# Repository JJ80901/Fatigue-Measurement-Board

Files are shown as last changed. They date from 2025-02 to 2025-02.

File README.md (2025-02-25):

# Fatigue-Measurement-Board
**Precision Displacement Sensing**

This board is designed to process and digitize a ±10V analog signal from a laser displacement sensor, ensuring high-fidelity data acquisition for fatigue testing applications. 

The signal enters through a BNC connector, passes through ESD protection and an RF filter, and is then scaled down to a ±1.65V range using a resistor divider. A non-inverting summing amplifier shifts the signal into a 0-3.3V range, with a 1.65V bias generated by an op-amp follower from a half-resistor divider off the 3.3V power rail.

To prevent aliasing, the conditioned signal passes through a third-order Butterworth Sallen-Key low-pass filter with a 5kHz cutoff frequency, optimized for sampling rates up to 1kHz. The filtered signal is digitized by an ADC141S626 14-bit ADC, which interfaces over SPI with an STM32F103CBT6 microcontroller, responsible for managing data acquisition and transmission.

Power is regulated using a TLV62569 switching regulator for 3.3V conversion and an HT7533-1 LDO, ensuring clean and stable power for the analog front end and microcontroller. 

This design improves upon earlier iterations by incorporating better filtering, precise voltage scaling, and a high-resolution ADC, making it ideal for fatigue analysis, precision displacement measurement, and other high-accuracy signal acquisition applications.

---

### What you'll find in this repository:
- Hardware designs (made in KiCad)
- STM32 Application Notes
- Device datasheets
- Circuit simulations

---

### Repository Project Structure:
- *3D Models* - Models for PCB components not found in the standard KiCad library
- *BOM* - An interactive HTML bill of materials (generated from the *Interactive HTML BOM* Plugin)
- *Datasheets* - Datasheets for specific devices used, such as the buck converter, LDO, Op-Amp, etc.
- *Docs* - STM32 application notes for crystal and USB design
- *Fatigue Test Board* - KiCad design files
- *Images* - High quality renderings of the final PCB in 3D
- *Libraries* - Folders to include schematic symbols and footprints for components not found in the standard KiCad library
- *Outputs* - Gerber files for manufacturing the PCB
- *Schematics* - PDFs of entire PCB schematic
- *Simulations* - LTSpice simulation block with any custom component libraries

---
***Disclaimer**: This board is ordered, but not yet tested!*

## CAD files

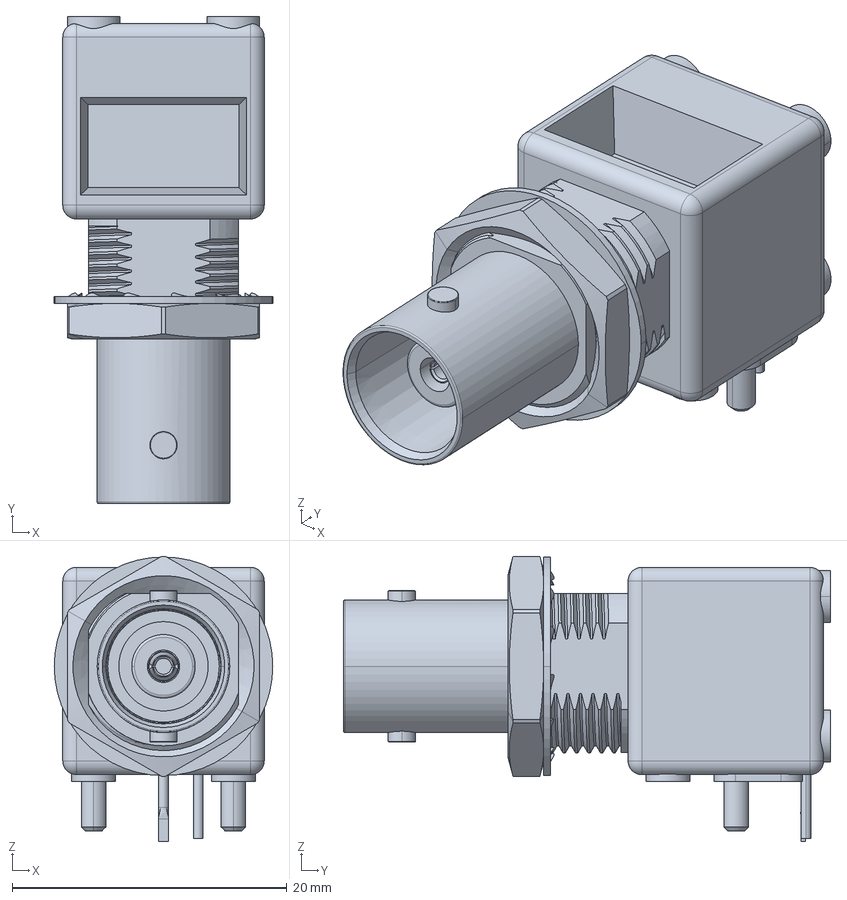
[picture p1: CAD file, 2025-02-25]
3D Models/BNC.stp
15.9 x 35.4 x 20.8 mm

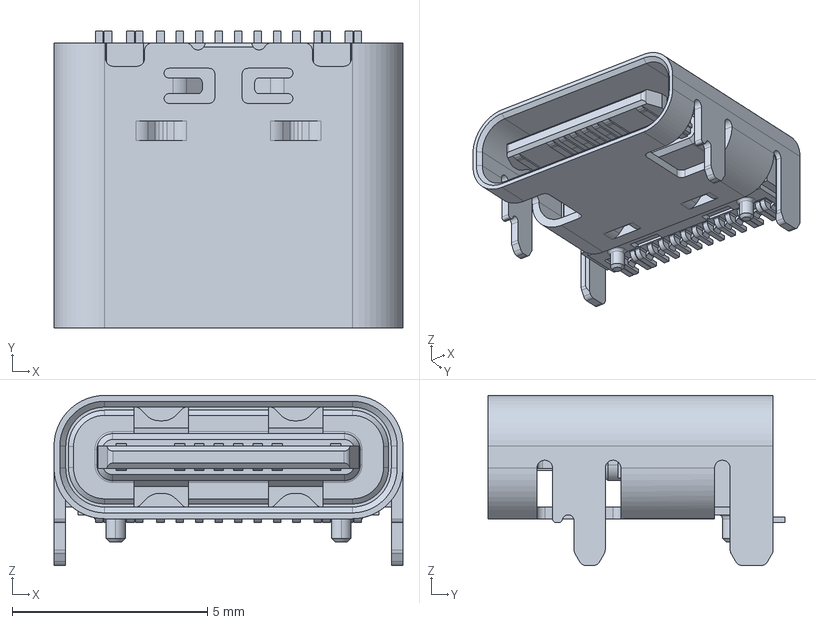
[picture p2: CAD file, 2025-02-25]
3D Models/USB-C.stp
8.94 x 7.60 x 4.36 mm

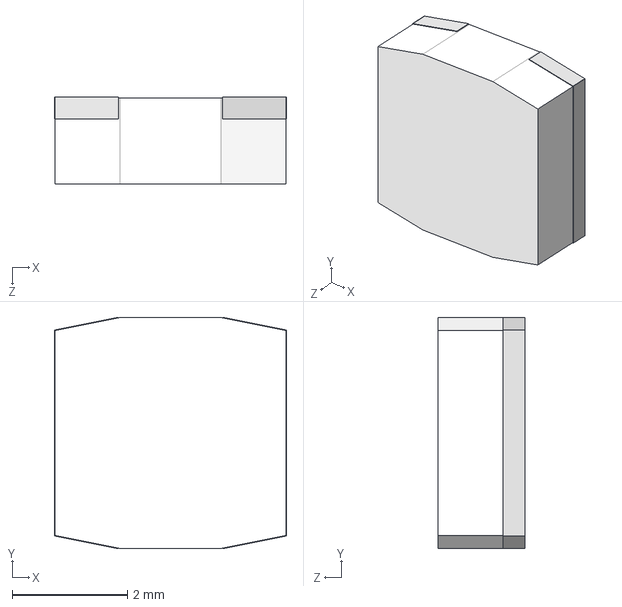
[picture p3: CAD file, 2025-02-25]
3D Models/PowerInductor.step
4.02 x 4.01 x 1.50 mm

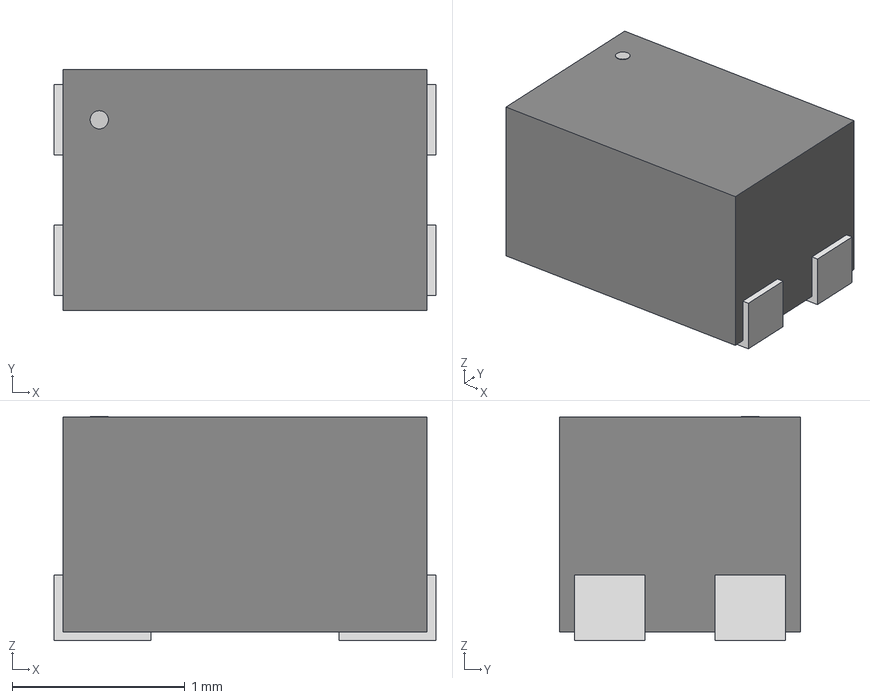
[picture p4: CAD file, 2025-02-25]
3D Models/CMC.step
2.21 x 1.40 x 1.30 mm

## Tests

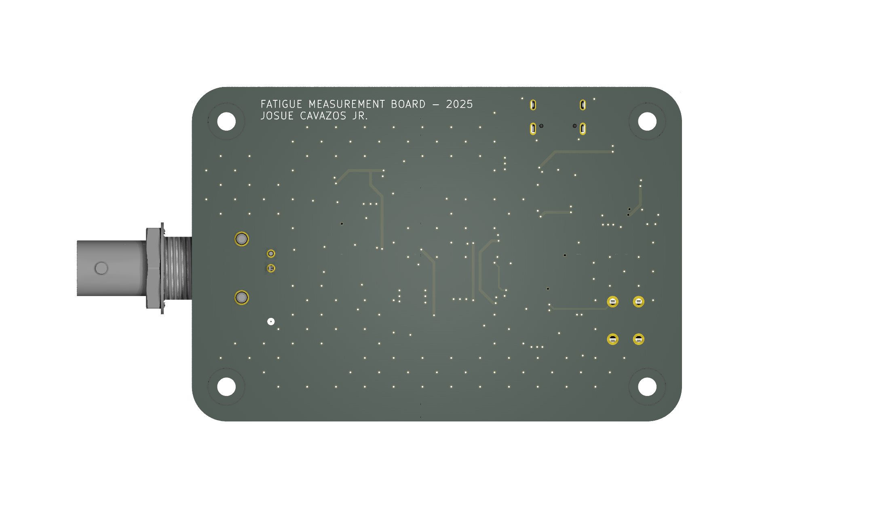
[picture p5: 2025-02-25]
Images/Fatigue Test Board Back.png

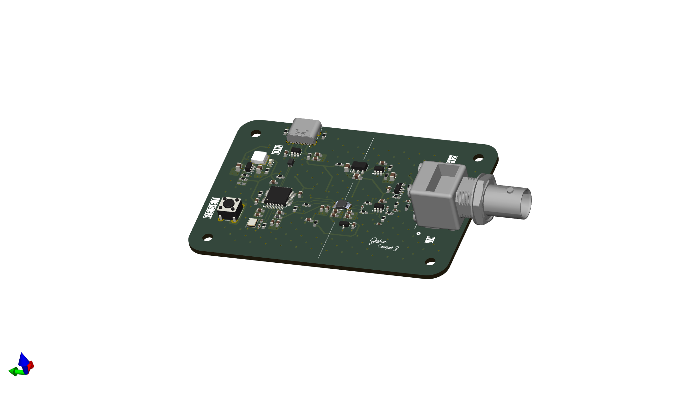
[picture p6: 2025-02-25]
Images/Fatigue Test Board Iso.png

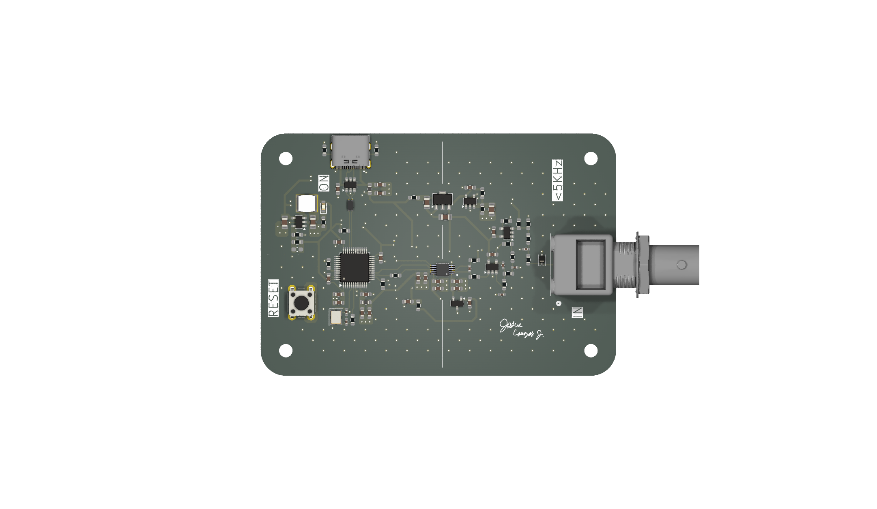
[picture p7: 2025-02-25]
Images/Fatigue Test Board Front.png

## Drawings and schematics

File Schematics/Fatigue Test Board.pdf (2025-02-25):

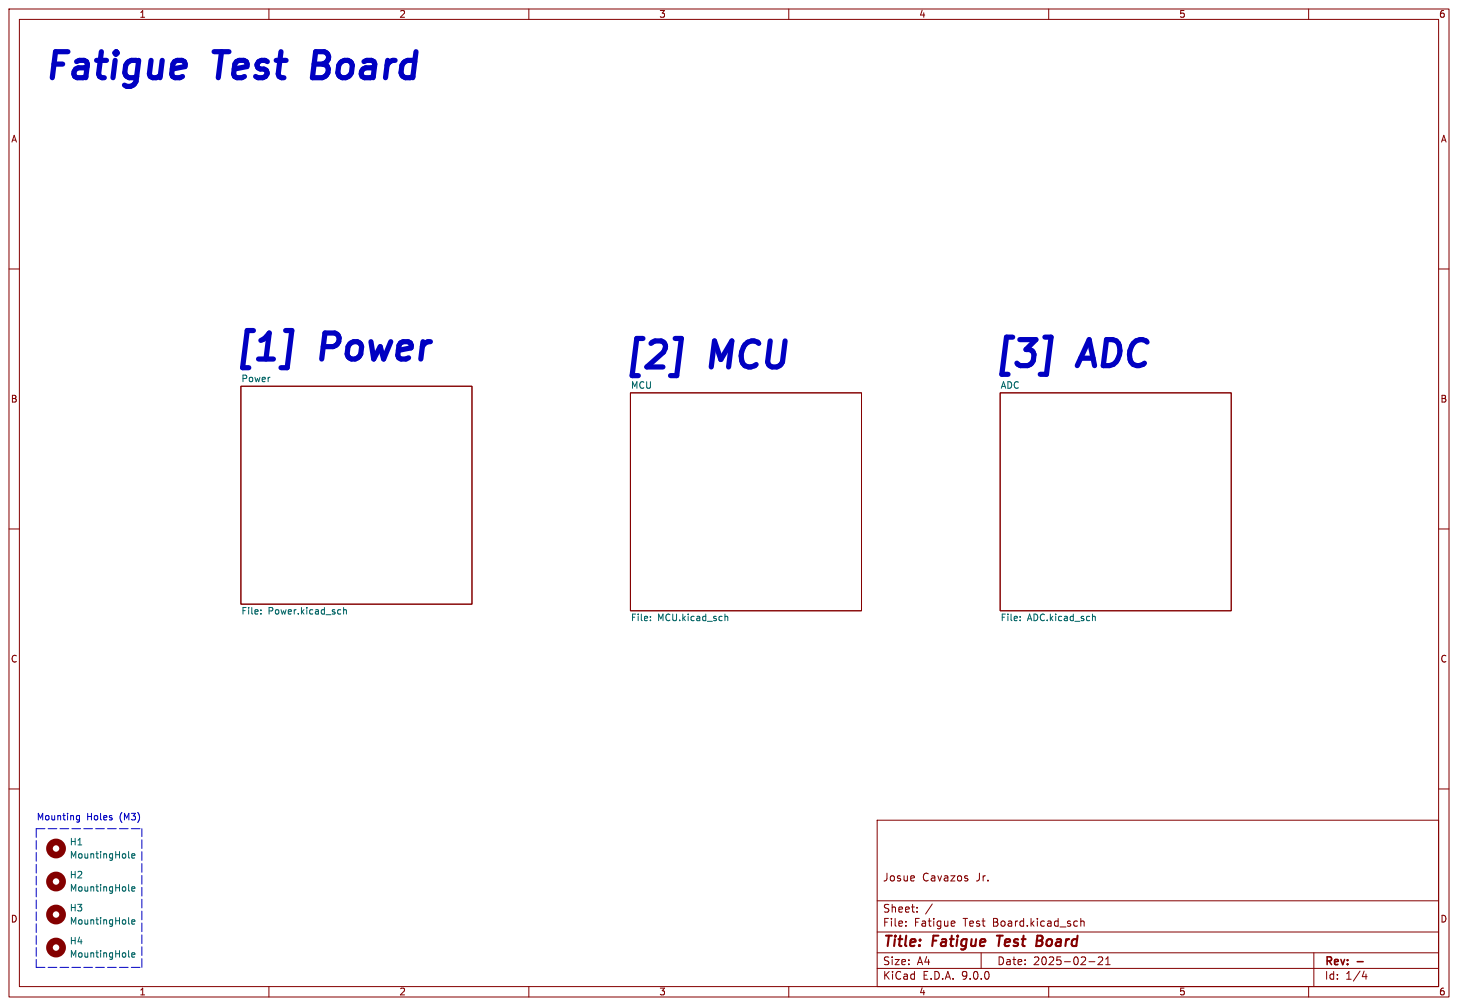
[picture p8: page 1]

File: ADC.kicad_sch H3 MountingHole H4 MountingHole H1 MountingHole H2 MountingHole

Id: 1/4 Title: Fatigue Test Board

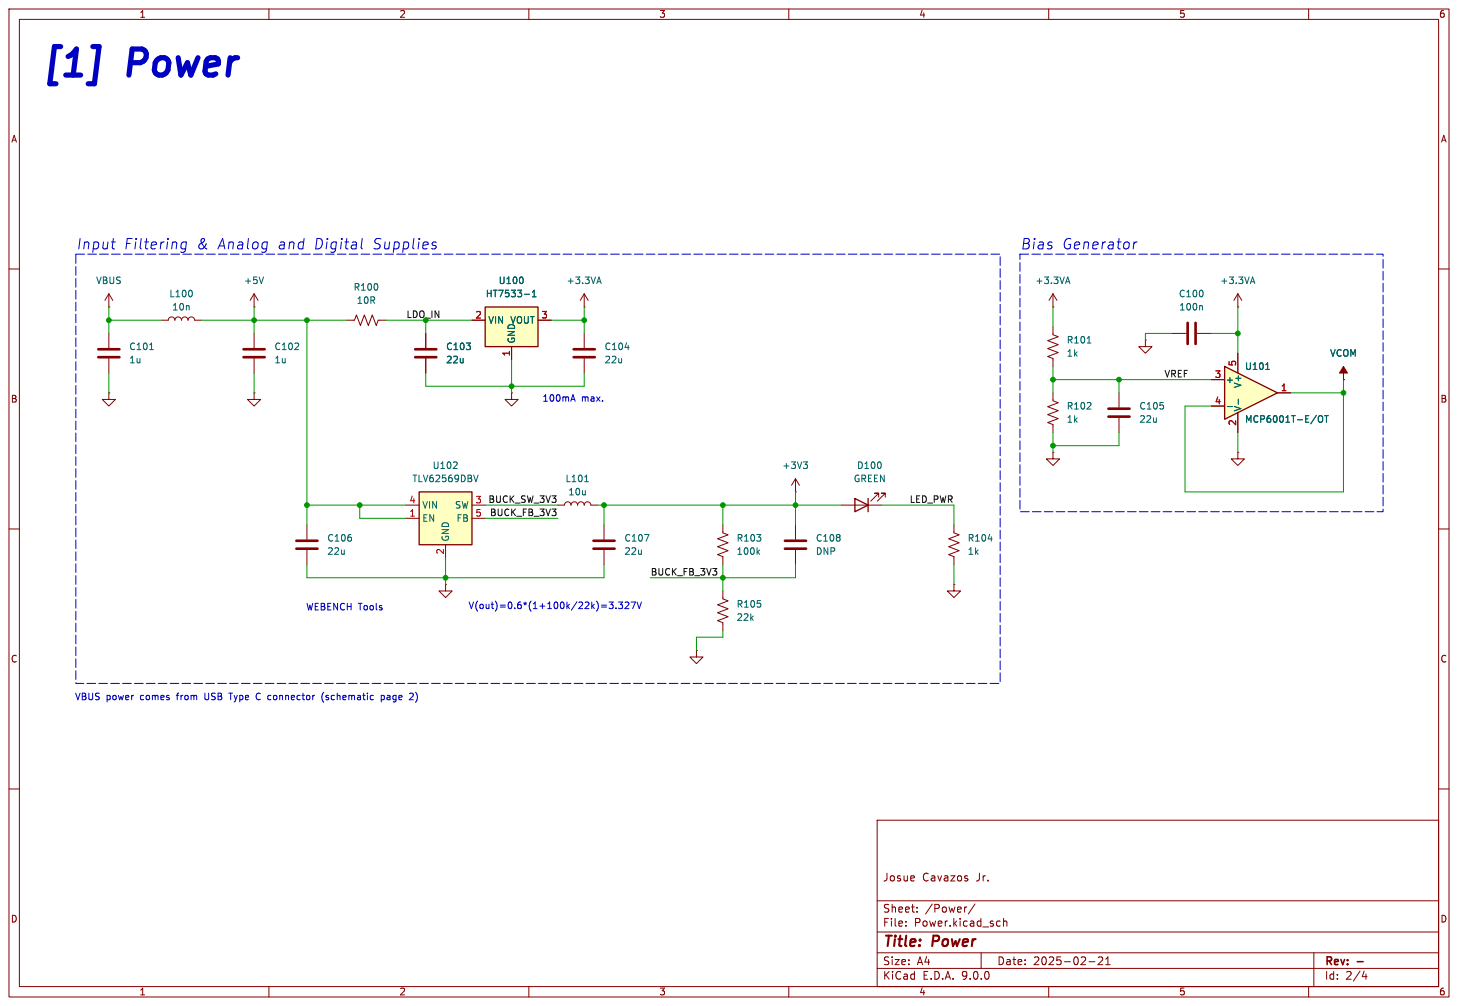
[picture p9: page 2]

Input Filtering & Analog and Digital Supplies

Id: 2/4 Title: Power File: Power.kicad_sch Sheet: /Power/ Josue Cavazos Jr.

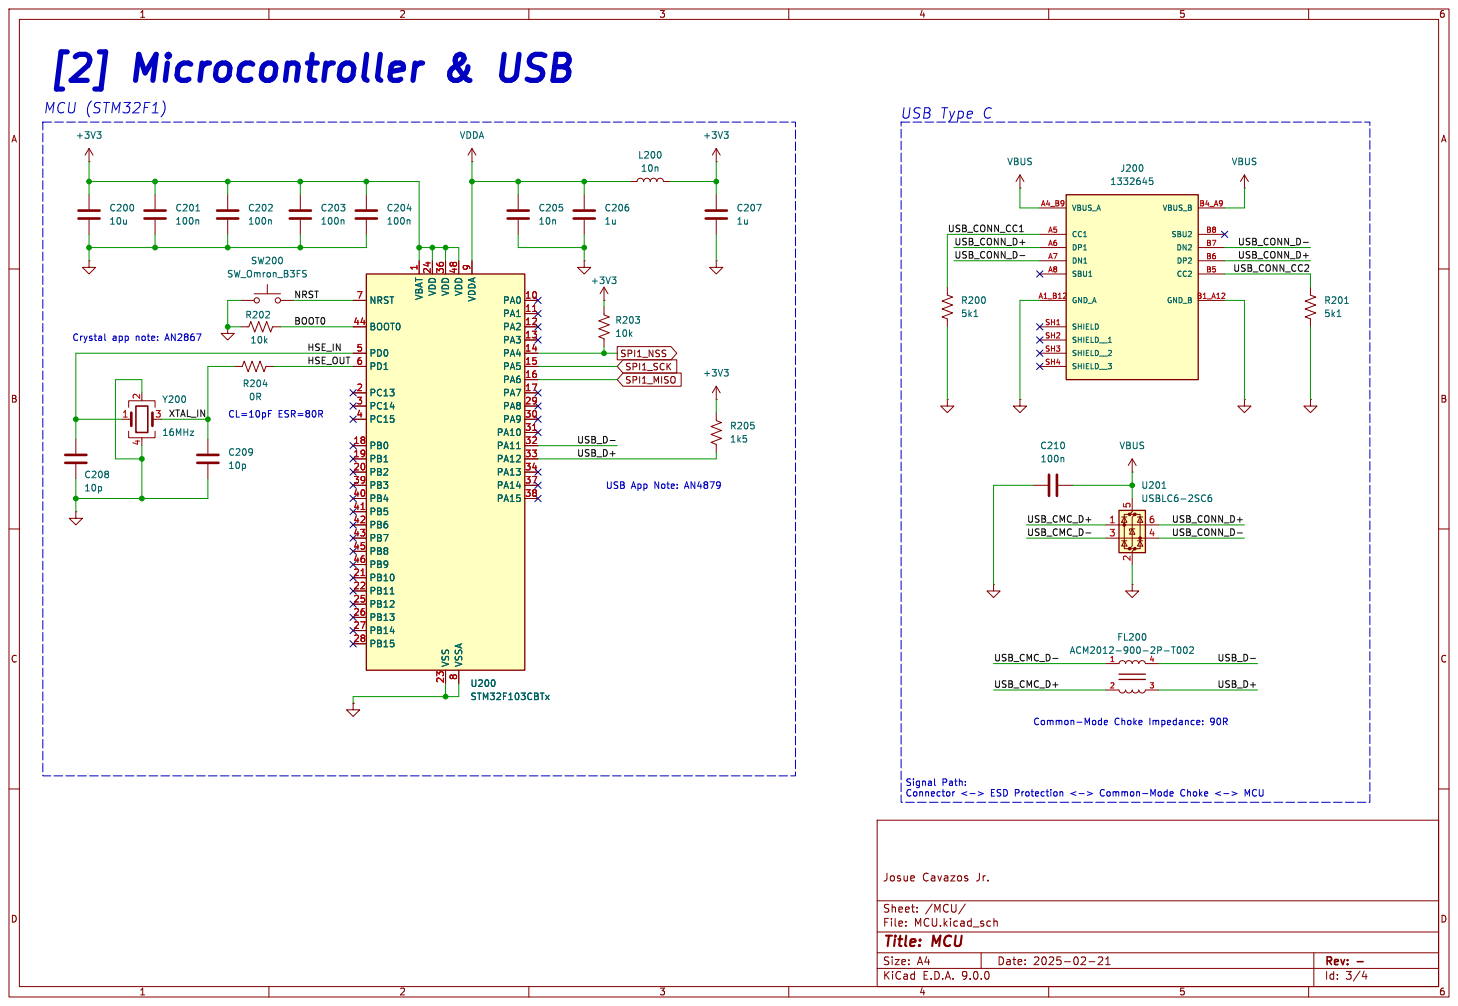
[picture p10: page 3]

1 VDD 24 VDD 36 VSS 23 VDD 48 VSSA

USB_CMC_D+ USB_D-USB App Note: AN4879 CL=10pF ESR=80R

File: MCU.kicad_sch Sheet: /MCU/ Josue Cavazos Jr.

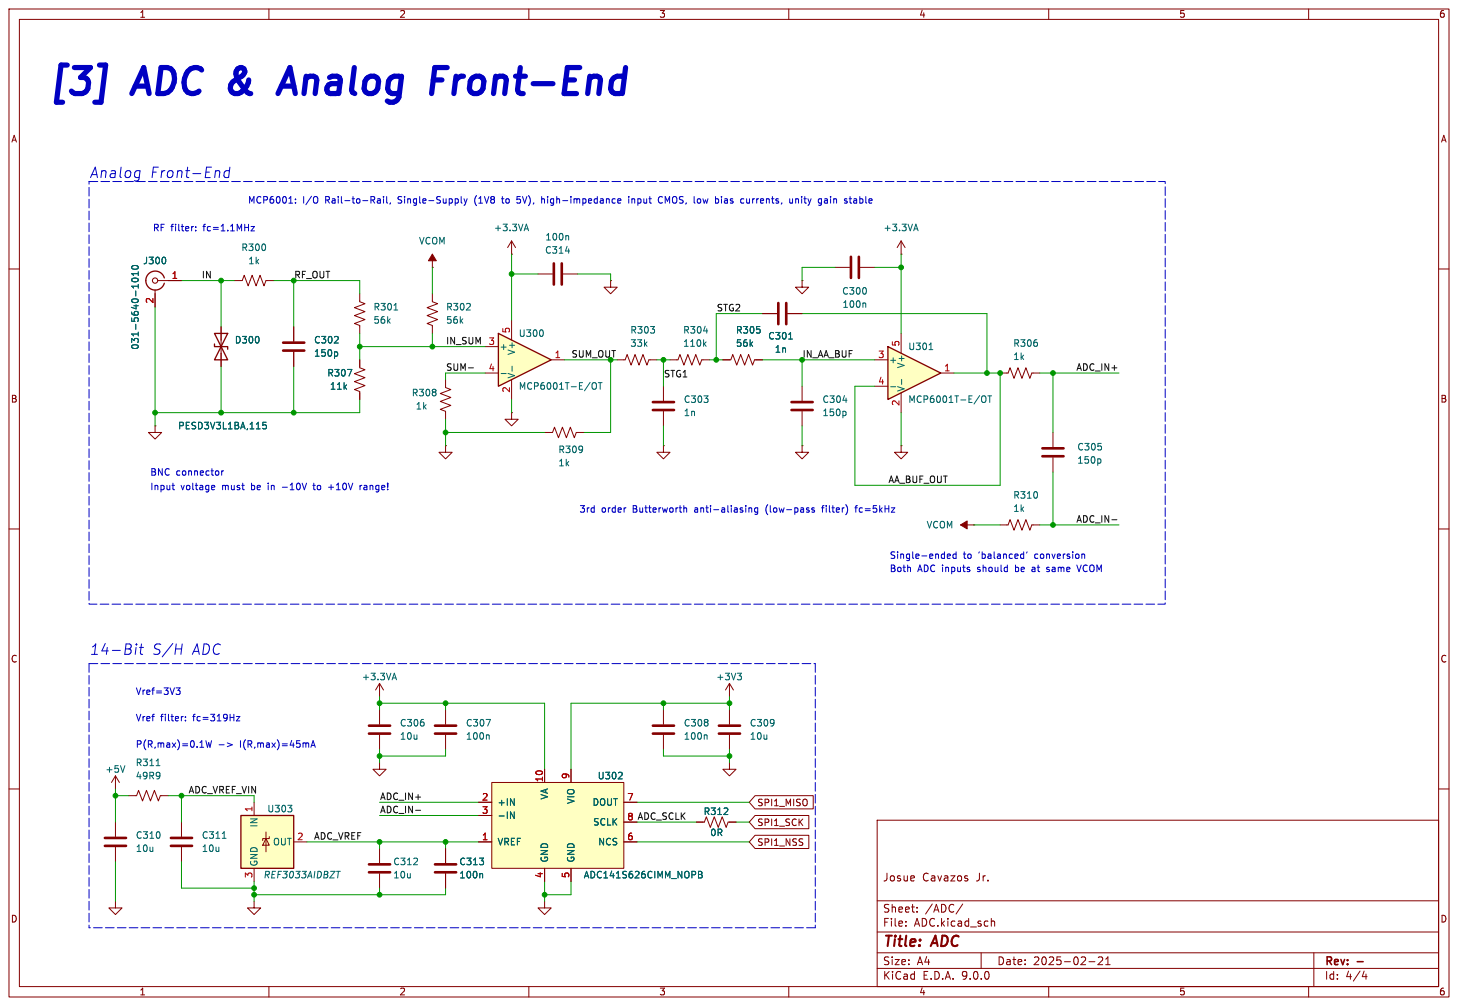
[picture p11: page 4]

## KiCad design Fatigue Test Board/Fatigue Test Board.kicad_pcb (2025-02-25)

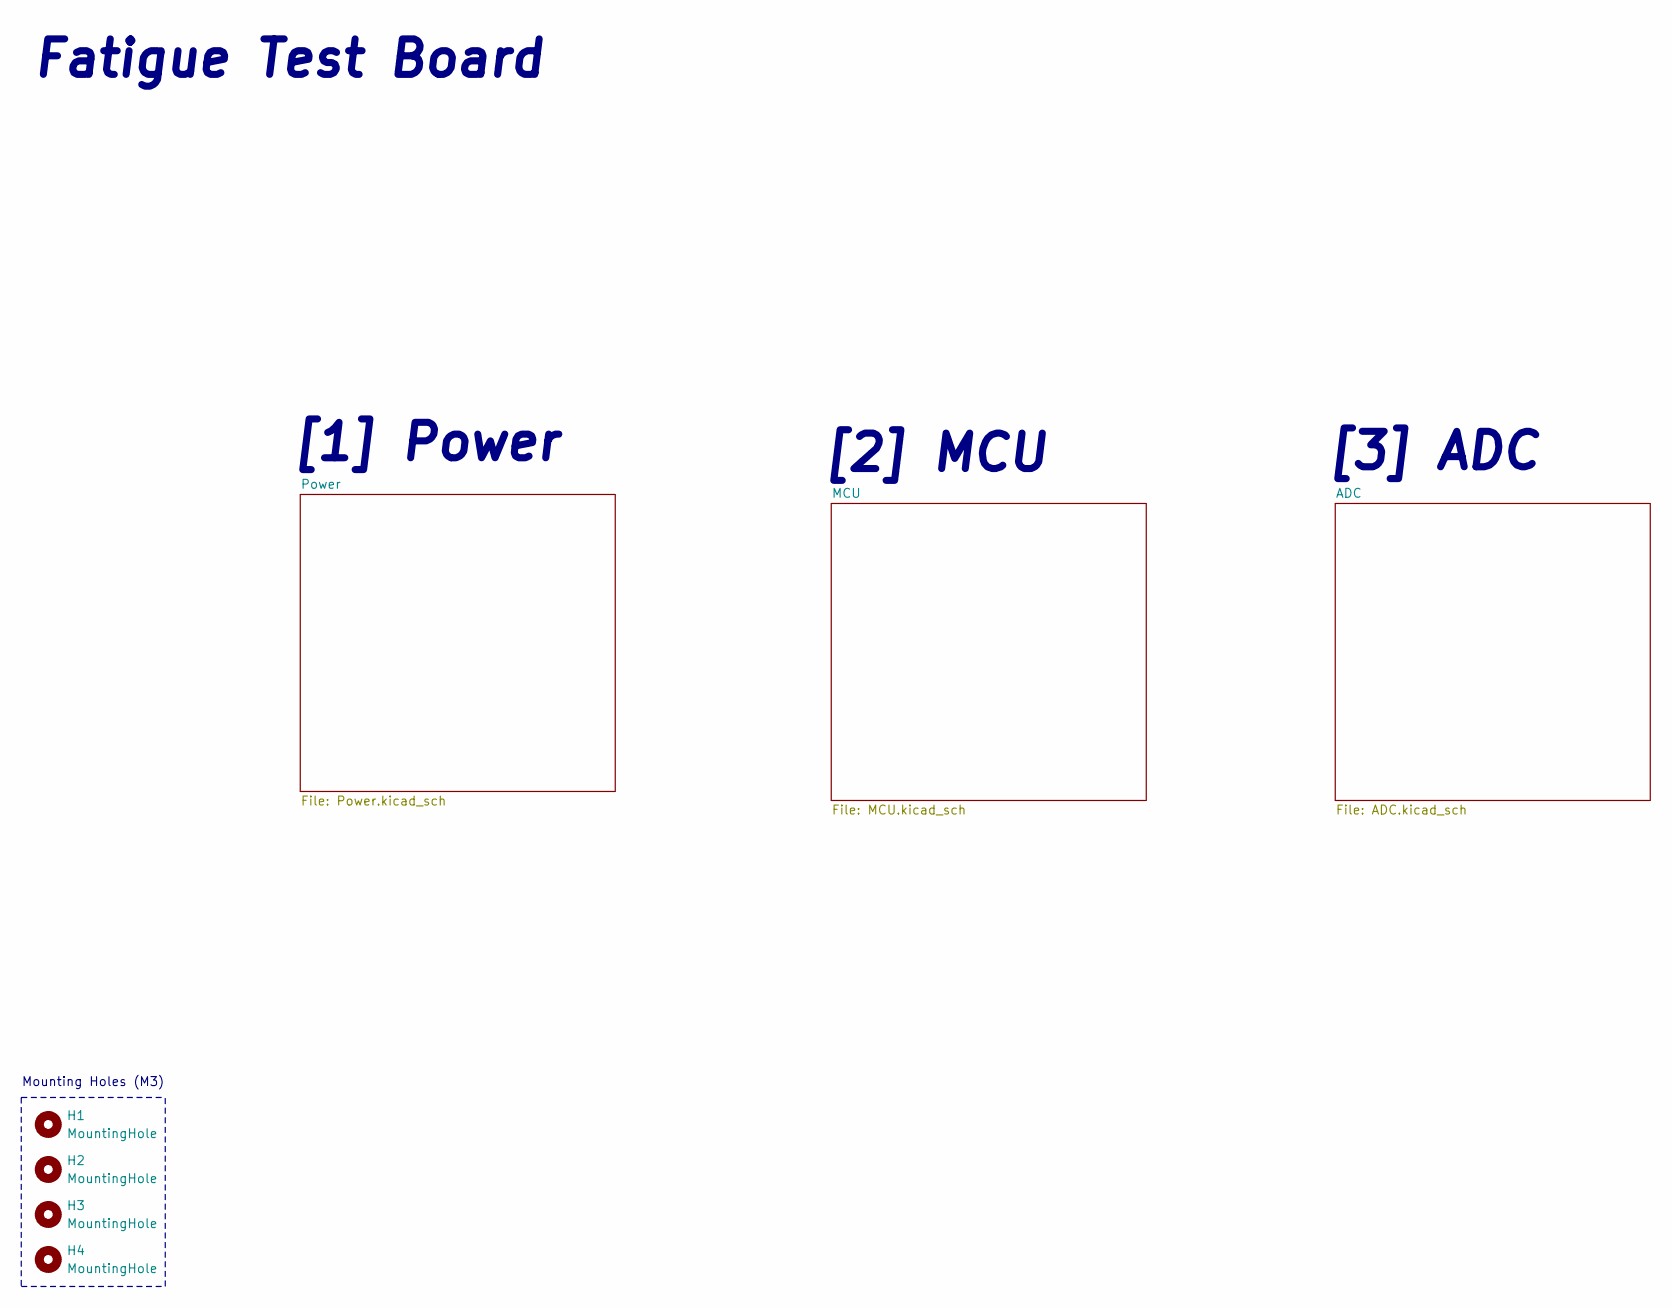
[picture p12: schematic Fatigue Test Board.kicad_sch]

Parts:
H1, H2, H3, H4: MountingHole; MountingHole_3.2mm_M3

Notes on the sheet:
[2] MCU
[3] ADC
Fatigue Test Board
[1] Power
Mounting Holes (M3)

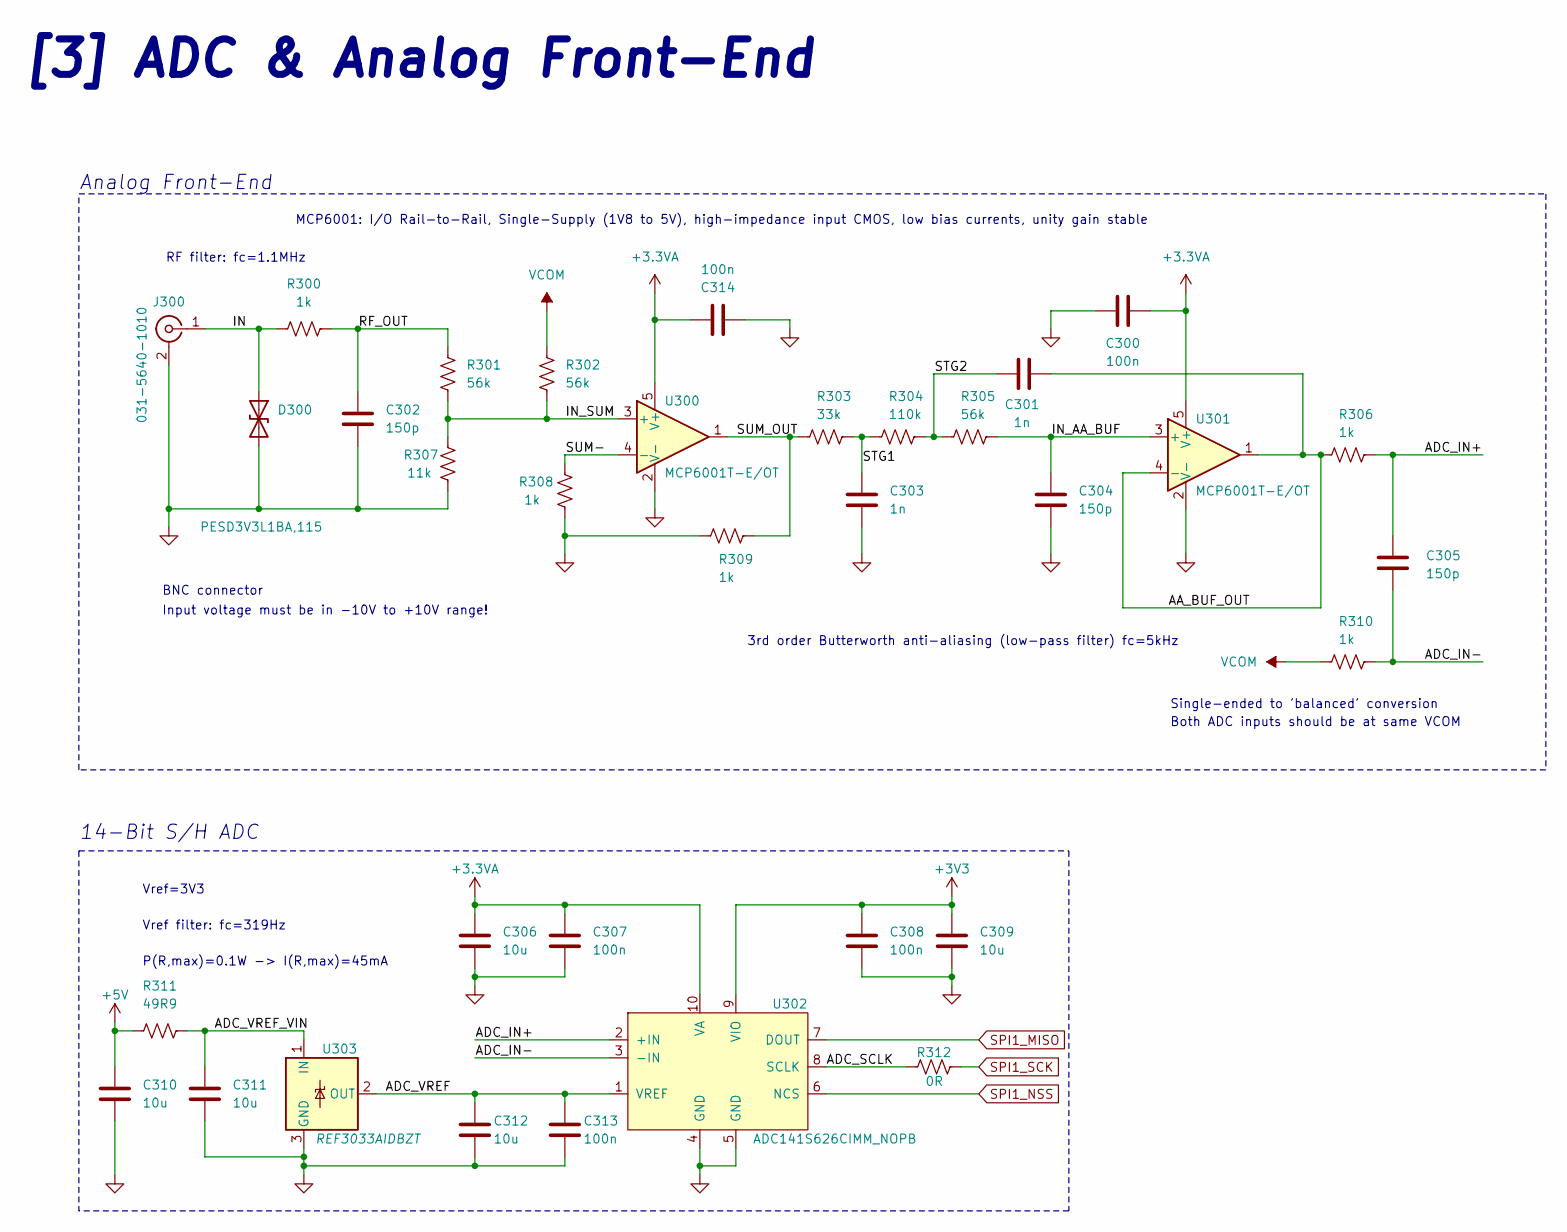
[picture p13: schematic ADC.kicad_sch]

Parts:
C300, C307, C308, C313, C314: 100n; C_0603_1608Metric_Pad1.08x0.95mm_HandSolder
C301, C303: 1n; C_0402_1005Metric_Pad0.74x0.62mm_HandSolder
C302, C304, C305: 150p; C_0402_1005Metric_Pad0.74x0.62mm_HandSolder
C306, C309, C310, C311, C312: 10u; C_0603_1608Metric_Pad1.08x0.95mm_HandSolder
D300: PESD3V3L1BA,115; D_SOD-323
J300: 031-5640-1010; CONN_73138-5033_MOL
R300, R306, R308, R309, R310: 1k; R_0603_1608Metric_Pad0.98x0.95mm_HandSolder
R301, R302, R305: 56k; R_0603_1608Metric_Pad0.98x0.95mm_HandSolder
R303: 33k; R_0603_1608Metric_Pad0.98x0.95mm_HandSolder
R304: 110k; R_0603_1608Metric_Pad0.98x0.95mm_HandSolder
R307: 11k; R_0603_1608Metric_Pad0.98x0.95mm_HandSolder
R311: 49R9; R_0603_1608Metric_Pad0.98x0.95mm_HandSolder
R312: 0R; R_0603_1608Metric_Pad0.98x0.95mm_HandSolder
U300, U301: MCP6001T-E/OT; SOT-23-5
U302: ADC141S626CIMM_NOPB; SOP50P490X110-10N
U303: REF3033AIDBZT; SOT-23

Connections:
+3.3VA: C300.1, C306.1, C307.1, C314.1, U300.5 (V+), U301.5 (V+), U302.10 (VA); also elsewhere on the board
+3V3: C308.1, C309.1, U302.9 (VIO); also elsewhere on the board
+5V: C310.1, R311.1; also elsewhere on the board
/ADC/AA_BUF_OUT: C301.2, R306.2, U301.1, U301.4 (-)
/ADC/ADC_IN+: C305.1, R306.1, U302.2 (+IN)
/ADC/ADC_IN-: C305.2, R310.1, U302.3 (-IN)
/ADC/ADC_SCLK: R312.2, U302.8 (SCLK)
/ADC/ADC_VREF: C312.1, C313.1, U302.1 (VREF), U303.2 (OUT)
/ADC/ADC_VREF_VIN: C311.1, R311.2, U303.1 (IN)
/ADC/IN: D300.1 (A1), J300.1 (In), R300.1
/ADC/IN_AA_BUF: C304.1, R305.1, U301.3 (+)
/ADC/IN_SUM: R301.2, R302.2, R307.1, U300.3 (+)
/ADC/RF_OUT: C302.1, R300.2, R301.1
/ADC/STG1: C303.1, R303.1, R304.2
/ADC/STG2: C301.1, R304.1, R305.2
/ADC/SUM-: R308.1, U300.4 (-)
/ADC/SUM_OUT: R303.2, R309.1, U300.1
GND: C300.2, C302.2, C303.2, C304.2, C306.2, C307.2, C308.2, C309.2, C310.2, C311.2, C312.2, C313.2, C314.2, D300.2 (A2), J300.2 (Ext), R307.2, R308.2, R309.2, U300.2 (V-), U301.2 (V-), U302.4 (GND), U302.5 (GND), U303.3 (GND); also elsewhere on the board
SPI1_MISO: U302.7 (DOUT); also elsewhere on the board
SPI1_NSS: U302.6 (NCS); also elsewhere on the board
SPI1_SCK: R312.1; also elsewhere on the board
VCOM: R302.1, R310.2; also elsewhere on the board

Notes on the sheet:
[3] ADC & Analog Front-End
RF filter: fc=1.1MHz
MCP6001: I/O Rail-to-Rail, Single-Supply (1V8 to 5V), high-impedance input CMOS, low bias currents, unity gain stable
3rd order Butterworth anti-aliasing (low-pass filter) fc=5kHz
P(R,max)=0.1W -> I(R,max)=45mA
Input voltage must be in -10V to +10V range!
Vref=3V3
Single-ended to 'balanced' conversion
Analog Front-End
Both ADC inputs should be at same VCOM
BNC connector
Vref filter: fc=319Hz
14-Bit S/H ADC

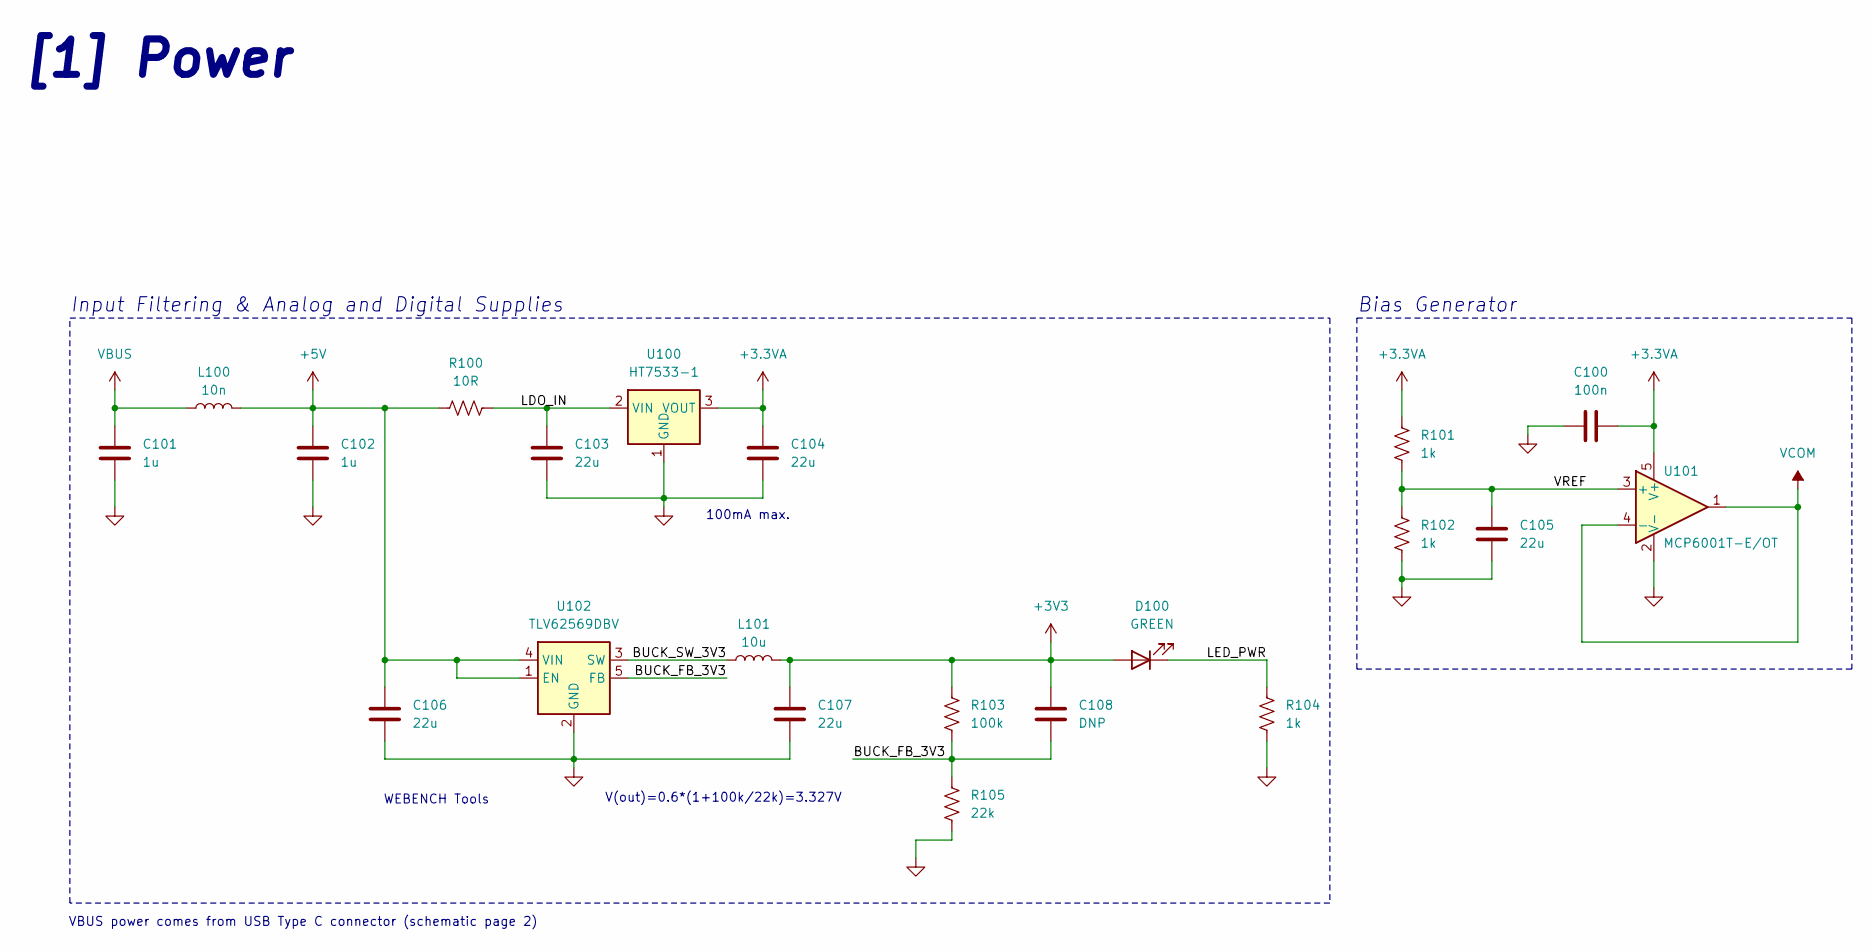
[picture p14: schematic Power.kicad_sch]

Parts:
C100: 100n; C_0603_1608Metric_Pad1.08x0.95mm_HandSolder
C101, C102: 1u; C_0603_1608Metric_Pad1.08x0.95mm_HandSolder
C103, C104, C105, C106, C107: 22u; C_0805_2012Metric_Pad1.18x1.45mm_HandSolder
C108: DNP; C_0603_1608Metric_Pad1.08x0.95mm_HandSolder
D100: GREEN; LED_0603_1608Metric_Pad1.05x0.95mm_HandSolder
L100: 10n; L_0603_1608Metric_Pad1.05x0.95mm_HandSolder
L101: 10u; IND_VLS4015CX-100M-H
R100: 10R; R_0603_1608Metric_Pad0.98x0.95mm_HandSolder
R101, R102, R104: 1k; R_0603_1608Metric_Pad0.98x0.95mm_HandSolder
R103: 100k; R_0603_1608Metric_Pad0.98x0.95mm_HandSolder
R105: 22k; R_0603_1608Metric_Pad0.98x0.95mm_HandSolder
U100: HT7533-1; SOT-89-3
U101: MCP6001T-E/OT; SOT-23-5
U102: TLV62569DBV; SOT-23-5

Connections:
+3.3VA: C100.2, C104.1, R101.2, U100.3 (VOUT), U101.5 (V+); also elsewhere on the board
+3V3: C107.1, C108.1, D100.2 (A), L101.2, R103.2; also elsewhere on the board
+5V: C102.1, C106.1, L100.2, R100.1, U102.1 (EN), U102.4 (VIN); also elsewhere on the board
/Power/BUCK_FB_3V3: C108.2, R103.1, R105.2, U102.5 (FB)
/Power/BUCK_SW_3V3: L101.1, U102.3 (SW)
/Power/LDO_IN: C103.1, R100.2, U100.2 (VIN)
/Power/LED_PWR: D100.1 (K), R104.2
/Power/VREF: C105.1, R101.1, R102.2, U101.3 (+)
GND: C100.1, C101.2, C102.2, C103.2, C104.2, C105.2, C106.2, C107.2, R102.1, R104.1, R105.1, U100.1 (GND), U101.2 (V-), U102.2 (GND); also elsewhere on the board
VBUS: C101.1, L100.1; also elsewhere on the board
VCOM: U101.1, U101.4 (-); also elsewhere on the board

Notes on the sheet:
V(out)=0.6*(1+100k/22k)=3.327V
Input Filtering & Analog and Digital Supplies
VBUS power comes from USB Type C connector (schematic page 2)
Bias Generator
100mA max.
WEBENCH Tools
[1] Power

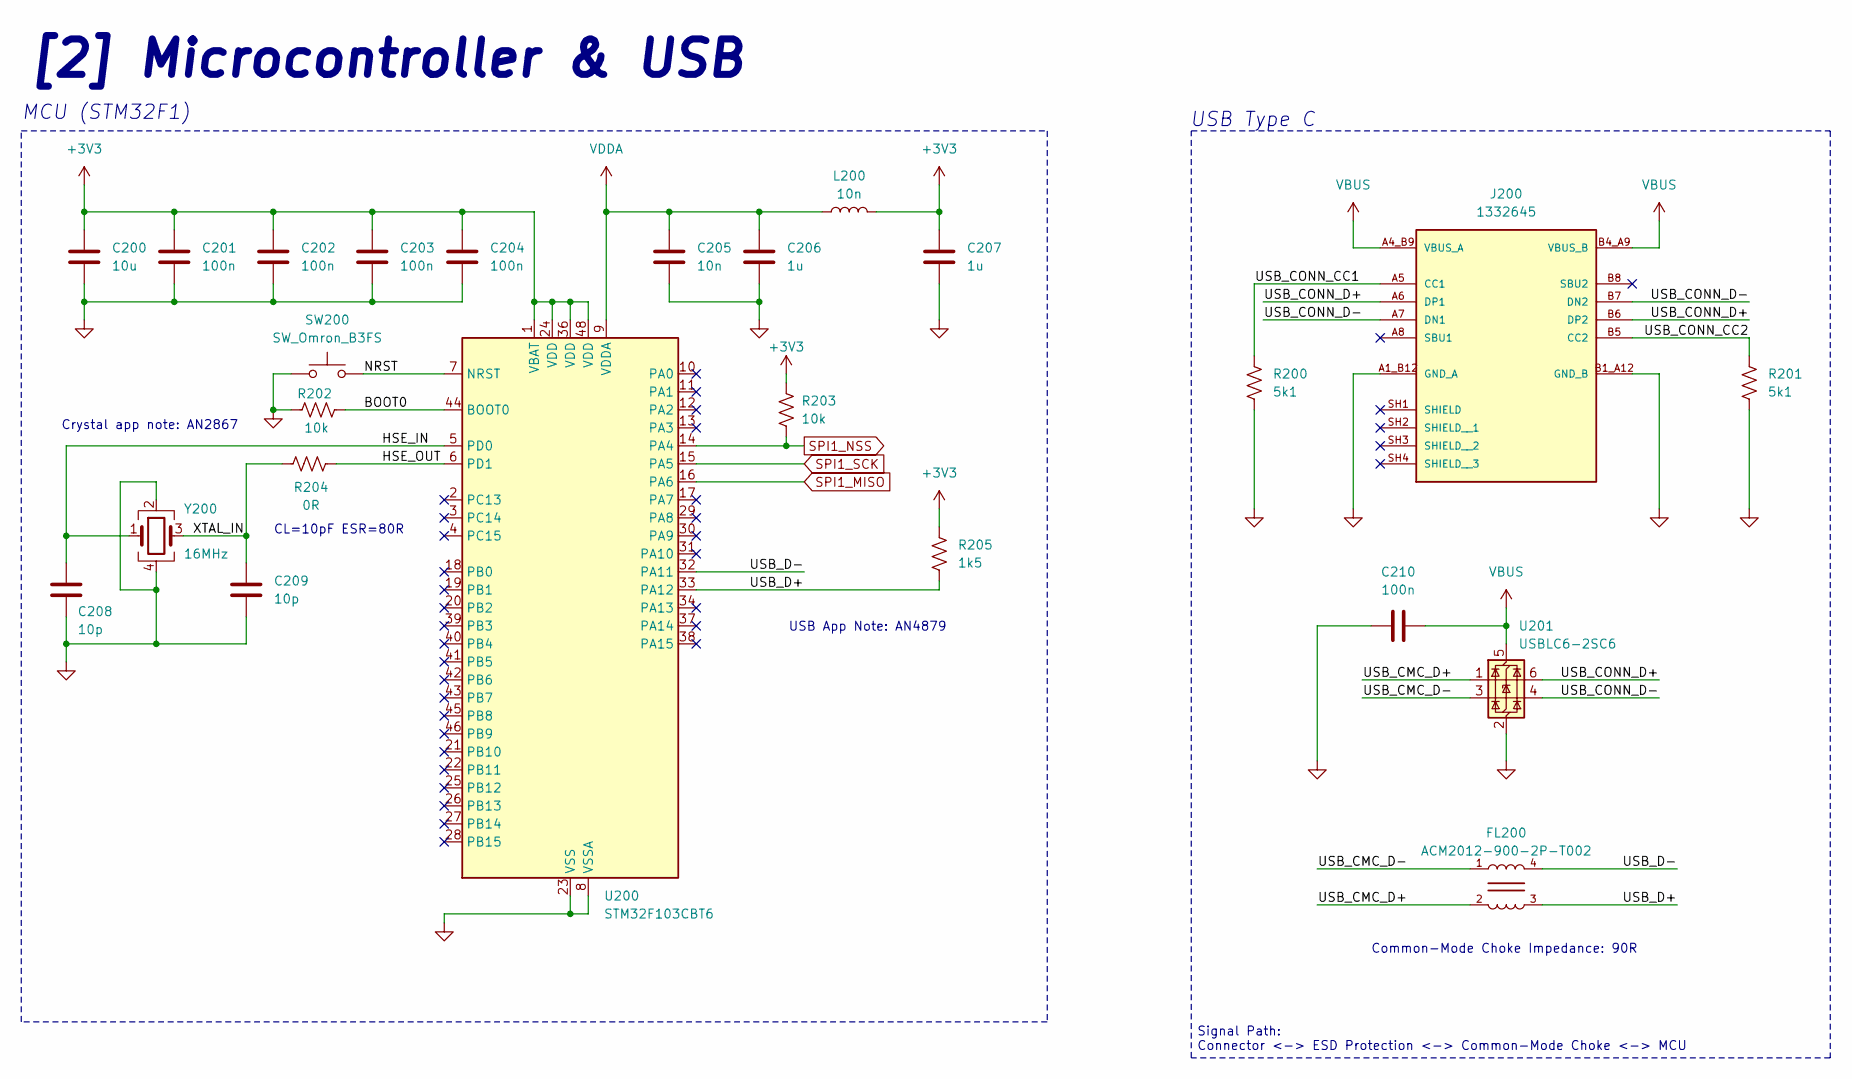
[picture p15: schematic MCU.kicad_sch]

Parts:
C200: 10u; C_0603_1608Metric_Pad1.08x0.95mm_HandSolder
C201, C202, C203, C204, C210: 100n; C_0603_1608Metric_Pad1.08x0.95mm_HandSolder
C205: 10n; C_0603_1608Metric_Pad1.08x0.95mm_HandSolder
C206, C207: 1u; C_0603_1608Metric_Pad1.08x0.95mm_HandSolder
C208, C209: 10p; C_0402_1005Metric_Pad0.74x0.62mm_HandSolder
FL200: ACM2012-900-2P-T002; FIL_ACM2012-900-2P-T002
J200: 1332645; PHOENIX_1332645; PARTREV 17.01.2022
L200: 10n; L_0603_1608Metric_Pad1.05x0.95mm_HandSolder
R200, R201: 5k1; R_0603_1608Metric_Pad0.98x0.95mm_HandSolder
R202, R203: 10k; R_0603_1608Metric_Pad0.98x0.95mm_HandSolder
R204: 0R; R_0603_1608Metric_Pad0.98x0.95mm_HandSolder
R205: 1k5; R_0603_1608Metric_Pad0.98x0.95mm_HandSolder
SW200: SW_Omron_B3FS; SW_PUSH_6mm
U200: STM32F103CBT6; LQFP-48_7x7mm_P0.5mm
U201: USBLC6-2SC6; SOT-23-6
Y200: 16MHz; Crystal_SMD_3225-4Pin_3.2x2.5mm

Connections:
+3V3: C200.1, C201.1, C202.1, C203.1, C204.1, C207.1, L200.2, R203.2, R205.1, U200.1 (VBAT), U200.24 (VDD), U200.36 (VDD), U200.48 (VDD); also elsewhere on the board
/MCU/BOOT0: R202.2, U200.44 (BOOT0)
/MCU/HSE_IN: C208.1, U200.5 (PD0), Y200.1
/MCU/HSE_OUT: R204.1, U200.6 (PD1)
/MCU/NRST: SW200.2, U200.7 (NRST)
/MCU/USB_CMC_D+: FL200.2, U201.1 (I/O1)
/MCU/USB_CMC_D-: FL200.1, U201.3 (I/O2)
/MCU/USB_CONN_CC1: J200.A5 (CC1), R200.1
/MCU/USB_CONN_CC2: J200.B5 (CC2), R201.1
/MCU/USB_CONN_D+: J200.A6 (DP1), J200.B6 (DP2), U201.6 (I/O1)
/MCU/USB_CONN_D-: J200.A7 (DN1), J200.B7 (DN2), U201.4 (I/O2)
/MCU/USB_D+: FL200.3, R205.2, U200.33 (PA12)
/MCU/USB_D-: FL200.4, U200.32 (PA11)
/MCU/XTAL_IN: C209.1, R204.2, Y200.3
GND: C200.2, C201.2, C202.2, C203.2, C204.2, C205.2, C206.2, C207.2, C208.2, C209.2, C210.2, J200.A1_B12 (GND_A), J200.B1_A12 (GND_B), R200.2, R201.2, R202.1, SW200.1, U200.8 (VSSA), U200.23 (VSS), U200.35 (VSS), U200.47 (VSS), U201.2 (GND), Y200.2, Y200.4; also elsewhere on the board
SPI1_MISO: U200.16 (PA6); also elsewhere on the board
SPI1_NSS: R203.1, U200.14 (PA4); also elsewhere on the board
SPI1_SCK: U200.15 (PA5); also elsewhere on the board
VBUS: C210.1, J200.A4_B9 (VBUS_A), J200.B4_A9 (VBUS_B), U201.5 (VBUS); also elsewhere on the board
VDDA: C205.1, C206.1, L200.1, U200.9 (VDDA)

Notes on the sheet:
Common-Mode Choke Impedance: 90R
CL=10pF ESR=80R
USB Type C
Signal Path: Connector <-> ESD Protection <-> Common-Mode Choke <-> MCU
Crystal app note: AN2867
[2] Microcontroller & USB
USB App Note: AN4879
MCU (STM32F1)

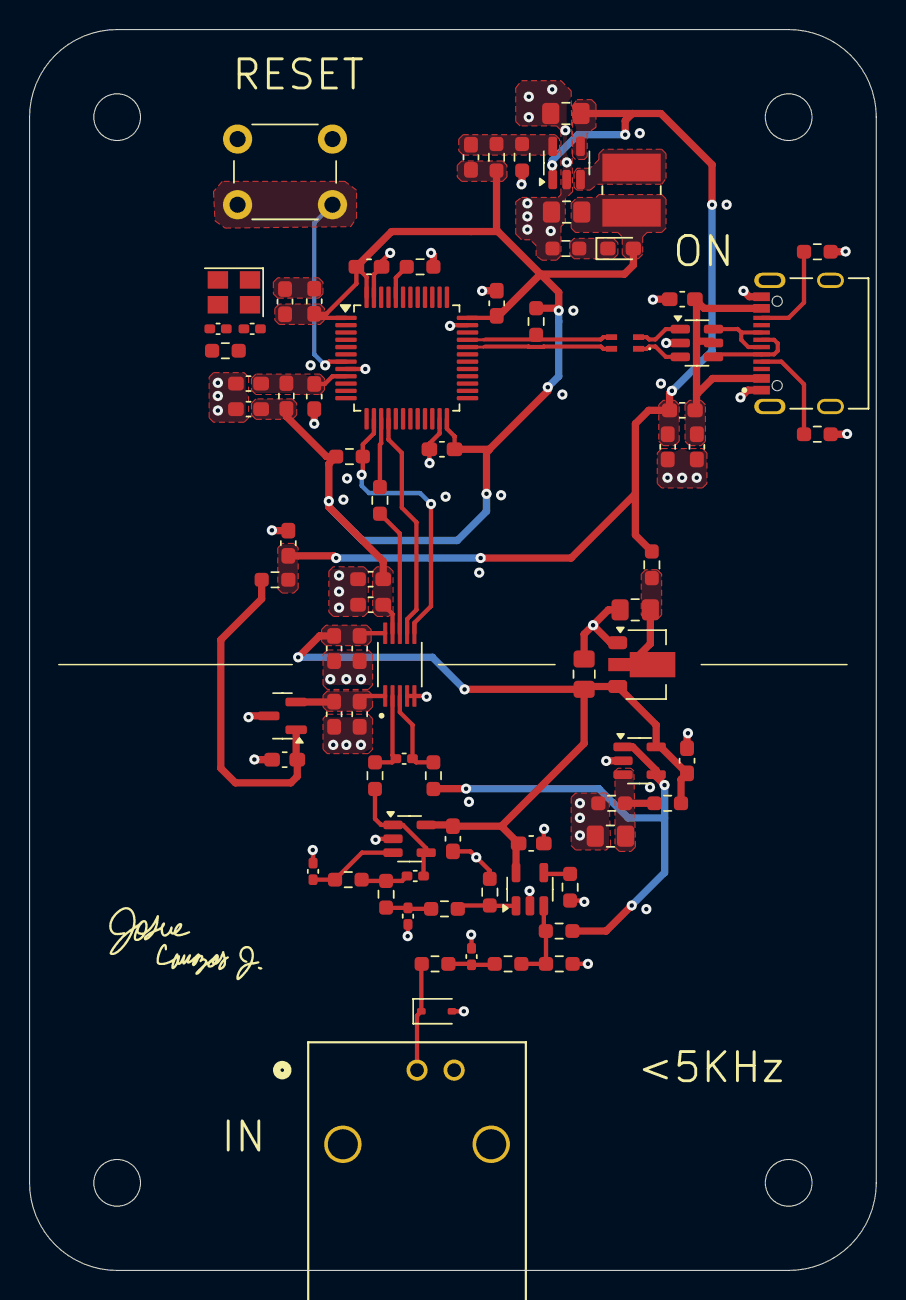
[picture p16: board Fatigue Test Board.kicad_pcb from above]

Board: 4 copper layers, 58.0 x 85.0 mm, 83 parts (0 on the bottom side), 42 nets.
